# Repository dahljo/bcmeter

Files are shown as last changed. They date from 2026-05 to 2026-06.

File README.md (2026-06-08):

## Legacy maintenance notice

This repository remains online so existing legacy Raspberry Pi bcMeter devices can keep updating from it. Its project status is **legacy maintenance**: it receives compatibility fixes for already deployed devices, but it is no longer the current Raspberry Pi bcMeter codebase.

For new setups and long-term maintenance, use the redesigned Raspberry Pi version: https://github.com/dahljo/bcmeter-pi.

The redesigned version was built from scratch for better maintainability, reliability, and setup/update workflows. Complete ready-to-flash Raspberry Pi images are available from https://bcmeter.org. Contact jd@bcmeter.org for questions.

## Thank you for your interest! This repository contains everything you need to build your own bcMeter (DIY) — freely available for private, educational and research use under CC BY-NC 4.0. For commercial use and licensing, please contact jd@bcmeter.org.

## Recommended software setup:
download bcMeter.img from https://bcmeter.org and clone that to a microSD card - change WiFi credentials within bcMeters hotspot mode and you're ready.

## manual software setup:

see https://bcmeter.org/wiki/index.php?title=Installation#Alternative:_Manual_Set_Up_the_microSD_Card for instructions, the basic procedure is:

1. write raspberry LITE(!) image to micro sd card with the help of the imager (https://www.raspberrypi.com/news/raspberry-pi-imager-imaging-utility/) - use the imager to configure SSH and WiFi BEFORE starting the write process!
2. bootup raspberry pi and log into it via ssh, download and run install.sh script:
wget -N https://raw.githubusercontent.com/dahljo/bcmeter/main/install.sh && sudo bash install.sh
3. run bcMeter script

### Script / Interface

install.sh is a just a batch to configure the raspberry for the use as bcMeter
bcMeter.py is the python script which saves the data as csv
/interface contains a d3.js interface for reading out the csv file

### Gerber for PCB Manufactoring

in /gerbers you'll find the gerbers for PCB manufactoring.

### STL files for 3D Printing

in /stl you find the files for 3d printing.

bcMeter Case

bcMeter PCB

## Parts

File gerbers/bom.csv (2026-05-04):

Designator | Footprint | Quantity | Value
C1 | 805 | 1 | 100nF
C10, C11, C12 | 805 | 3 | 1uF
C13 | 805 | 1 | 15nF
C15, C22 | 805 | 2 | 220pF
C16, C4 | 805 | 2 | 100nF
C17 | 805 | 1 | 10uF
C18 | 805 | 1 | 0.1uF
C20 | 1210 | 1 | 47uF
C21 | CP_Elec_6.3x5.8 | 1 | 470uF
C6, C9 | 805 | 2 | 5.6pF
D10, D11, D4, D6, D7 | D_SOD-123 | 5 | 1N5817
D12 | D_SMB | 1 | B230
D3 | 805 | 1 | Status LED
D5 | D_SMA | 1 | SS24
J1 | JST_SH_SM03B-SRSS-TB_1x03-1MP_P1.00mm_Horizontal | 1 | Omron D6F
J11 | JST_PH_B4B-PH-K_1x04_P2.00mm_Vertical | 1 | DISP
J12 | PinHeader_2x03_P2.54mm_Vertical | 1 | Conn_02x03_Counter_Clockwise
J13 | PinHeader_1x02_P2.54mm_Vertical | 1 | 5V Ext
J15 | BarrelJack_GCT_DCJ200-10-A_Horizontal | 1 | Jack-DC
J16, J18, J19, J20 | JST_EH_B4B-EH-A_1x04_P2.50mm_Vertical | 4 | Conn_01x04
J17 | JST_PH_B2B-PH-K_1x02_P2.00mm_Vertical | 1 | 12V Header for non pwm pump
J2 | JST_PH_B4B-PH-K_1x04_P2.00mm_Vertical | 1 | i2c opt
J3 | PinHeader_1x02_P2.54mm_Vertical | 1 | 3.3V Header
J5 | JST_XH_B2B-XH-A_1x02_P2.50mm_Vertical | 1 | Pump 5V Header NONPWM
J6 | PinSocket_2x20_P2.54mm_Vertical | 1 | Raspberry_Pi_2_3
J7 | JST_EH_B2B-EH-A_1x02_P2.50mm_Vertical | 1 | heater/fan
J8 | JST_XH_B3B-XH-A_1x03_P2.50mm_Vertical | 1 | Conn_01x03
L2 | L_Bourns_SRP7028A_7.3x6.6mm | 1 | 15uH
Q3, Q7, Q8 | SOT-23 | 3 | MMBT3904
Q4, Q5, Q6 | SOT-23 | 3 | AO3400A
R1, R2, R7 | 805 | 3 | 3k3
R11, R6 | 805 | 2 | 5K
R12, R13 | 805 | 2 | 100R
R14 | 805 | 1 | 10k2R
R15 | 805 | 1 | 1k7
R19, R4 | 805 | 2 | 150
R20, R21 | 805 | 2 | 75
R22, R25, R5 | 805 | 3 | 10k
R23, R24 | 805 | 2 | 68
R26, R27 | 805 | 2 | 100k
R3 | 805 | 1 | 5
R8 | 805 | 1 | 30.9K
SW1 | PinHeader_2x01_P2.54mm_Vertical | 1 | Button
U1 | SOIC-8_3.9x4.9mm_P1.27mm | 1 | MCP6022
U3 | Sensirion_DFN-4_1.5x1.5mm_P0.8mm_SHT4x_NoCentralPad | 1 | SHT4x
U4 | SSOP-20_3.9x8.7mm_P0.635mm | 1 | ADS8344N
U5 | SOIC-8-1EP_3.9x4.9mm_P1.27mm_EP2.62x3.51mm | 1 | TPS54233
U6 | SOIC-8_3.9x4.9mm_P1.27mm | 1 | MCP1501-40xSN

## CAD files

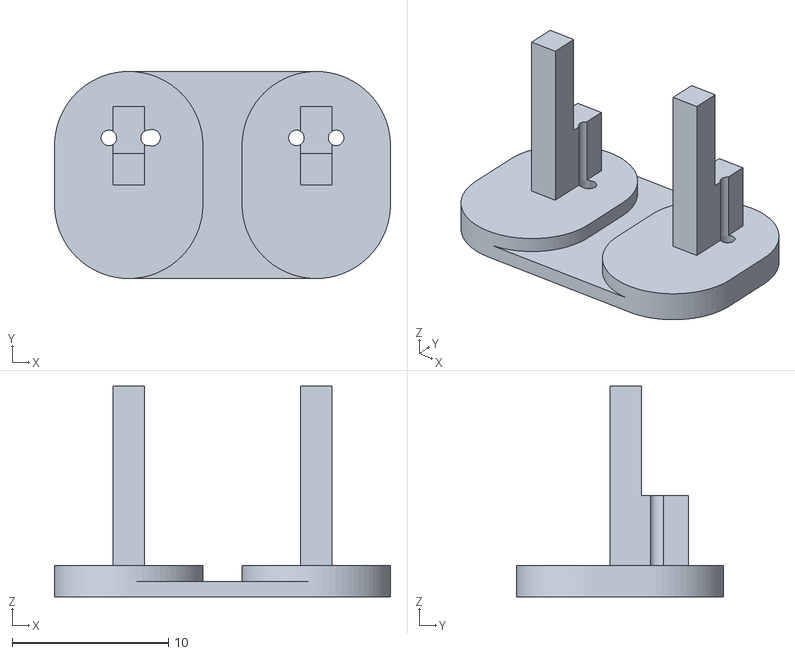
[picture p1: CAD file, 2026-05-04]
stl/bcMeter_sensorbracket.stl
21.5 x 13.2 x 13.5

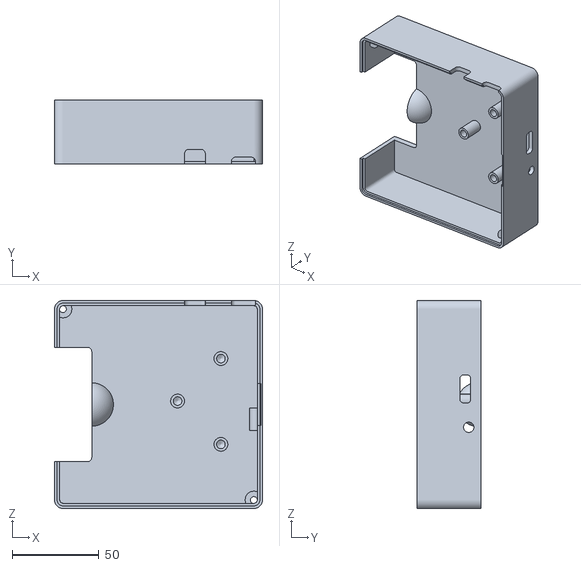
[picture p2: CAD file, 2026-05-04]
stl/bcMeter_iot_topcase.stl
120.0 x 37.0 x 120.0

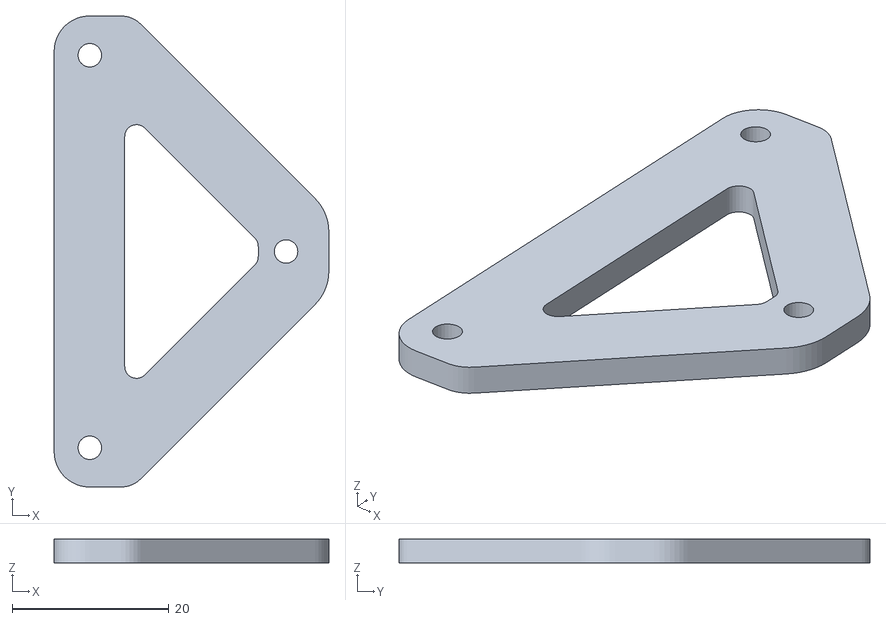
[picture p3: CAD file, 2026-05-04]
stl/bcmeter-sps30-bracket.stl
35.0 x 60.0 x 3.00

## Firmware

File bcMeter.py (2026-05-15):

import glob
import os
import re
import signal
import socket
import shutil
import subprocess
import sys
import typing
from collections import deque
from datetime import datetime
from pathlib import Path
from threading import Thread, Event, Lock
from time import sleep, time

import numpy
import pigpio
import RPi.GPIO as GPIO
import smbus
import spidev

from bcMeter_shared import (
	config_json_handler,
	check_connection,
	manage_bcmeter_status,
	show_display,
	config,
	i2c,
	setup_logging,
	run_command,
	send_email,
	update_config,
	filter_values_ona,
	apply_dynamic_airflow,
	can_send_mail,
	get_session_flag,
	set_session_flag
)

sps30_available = False
sps30_sensor = None

bcMeter_version = "1.1.5 2026-05-15"
base_dir = '/home/bcmeter' if os.path.isdir('/home/bcmeter') else '/home/bcMeter' if os.path.isdir('/home/bcMeter') else '/home/pi'

logger = setup_logging('bcMeter')
debug = True if (len(sys.argv) > 1) and (sys.argv[1] == "debug") else False
if debug:
	logger.debug("--- DEBUG MODE ENABLED ---")
logger.debug(config)
logger.debug(f"bcMeter Version {bcMeter_version}")
bus = smbus.SMBus(1)
i2c_lock = Lock()

import bcMeter_shared
bcMeter_shared.i2c_lock = i2c_lock

try:
	from sps30_i2c import SPS30
	_sps = SPS30(bus=1, i2c_lock=i2c_lock)
	_sps.start()
	sleep(1)
	for _ in range(5):
		if _sps.data_ready():
			sps30_available = True
			sps30_sensor = _sps
			break
		sleep(0.5)
	if not sps30_available:
		_sps.stop()
		_sps.close()
except Exception as e:
	if debug:
		print(f"SPS30 init failed: {e}")
	sps30_available = False

if sps30_available:
	logger.info("SPS30 PM sensor detected and initialized")

NUM_CHANNELS = config.get('num_channels', 1)
LED_880NM_PIN = 26
LED_520NM_PIN = 25
LED_370NM_PIN = 24
BUSY_PIN = 17

CHANNELS_CONFIG = {
	'880nm': {'pin': LED_880NM_PIN, 'sigma': 7.77e-8, 'sens': 0, 'ref': 0, 'atn': 0, 'bc': 0, 'bc_unfiltered': 0},
	'520nm': {'pin': LED_520NM_PIN, 'sigma': 13.14e-8, 'sens': 0, 'ref': 0, 'atn': 0, 'bc': 0, 'bc_unfiltered': 0},
	'370nm': {'pin': LED_370NM_PIN, 'sigma': 18.47e-8, 'sens': 0, 'ref': 0, 'atn': 0, 'bc': 0, 'bc_unfiltered': 0},
}
WAVELENGTH_ORDER = ['880nm', '520nm', '370nm']

disable_pump_control = config.get('disable_pump_control', False)
get_location = config.get('get_location', False)
heating = config.get('heating', False)
pump_pwm_freq = int(config.get('pwm_freq', 20))
af_sensor_type = int(config.get('af_sensor_type', 1))
use_rgb_led = config.get('use_rgb_led', 0)
use_display = config.get('use_display', False)
airflow_sensor = config.get('airflow_sensor', False)
pump_dutycycle = int(config.get('pump_dutycycle', 20))
reverse_dutycycle = config.get('reverse_dutycycle', False)
sample_spot_diameter = float(str(config.get('sample_spot_diameter', 0.4)).replace(',', '.'))
is_ebcMeter = config.get('is_ebcMeter', False)
mail_logs_to = config.get('mail_logs_to', "")
send_log_by_mail = config.get('send_log_by_mail', False)
filter_status_mail = config.get('filter_status_mail', False)
disable_led = config.get('disable_led', False)
airflow_type = int(config.get('af_sensor_type', 1))
TWELVEVOLT_ENABLE = config.get('TWELVEVOLT_ENABLE', False)
twelvevolt_duty = config.get('twelvevolt_duty', 20)
automatic_airflow_control = config.get('automatic_airflow_control', False)
spi_vref=config.get('spi_vref', 4.096)

iot_enable=config.get('iot_enable', False)

bc_data_history = {
	'unfiltered': {wl: [] for wl in WAVELENGTH_ORDER},
	'filtered': {wl: [] for wl in WAVELENGTH_ORDER},
	'all_log_data': []
}
current_measured_airflow_lpm = 0.0
desired_airflow_in_lpm = float(str(config.get('airflow_per_minute', 0.1)).replace(',', '.'))

_bc_filter_state = {}

def filter_bc_values():
	global bc_data_history, is_ebcMeter, WAVELENGTH_ORDER, _bc_filter_state
	kernel = 3 if is_ebcMeter else 5
	state = _bc_filter_state
	if state.get('kernel') != kernel or not state.get('windows'):
		state['kernel'] = kernel
		state['windows'] = {wl: deque(maxlen=kernel) for wl in WAVELENGTH_ORDER}
		state['processed'] = {wl: 0 for wl in WAVELENGTH_ORDER}
		for wl in WAVELENGTH_ORDER:
			bc_data_history['filtered'][wl] = []
	for wl in WAVELENGTH_ORDER:
		unfiltered = bc_data_history['unfiltered'][wl]
		processed = state['processed'].get(wl, 0)
		if processed > len(unfiltered):
			processed = 0
			state['windows'][wl].clear()
			bc_data_history['filtered'][wl] = []
		window = state['windows'][wl]
		for v in unfiltered[processed:]:
			window.append(v)
			med = numpy.median(list(window))
			bc_data_history['filtered'][wl].append(float(med) if is_ebcMeter else int(med))
		state['processed'][wl] = len(unfiltered)


class ADS8344:
	START_BIT = 0x80
	SINGLE_END = 0x04
	CLOCK_INTERNAL = 0x02
	CHANNELS = {
		0: 0x00, 1: 0x04, 2: 0x01, 3: 0x05,
		4: 0x02, 5: 0x06, 6: 0x03, 7: 0x07
	}

	def __init__(self, bus=0, device=0, vref=spi_vref, busy_pin=None):
		self.spi = spidev.SpiDev()
		self.busy_pin = busy_pin
		try:
			self.spi.open(bus, device)
			self.spi.max_speed_hz = 1000000
			self.spi.mode = 0
			self.vref = vref
			if self.busy_pin is not None:
				GPIO.setup(self.busy_pin, GPIO.IN, pull_up_down=GPIO.PUD_UP)
			self.initialized = True
		except Exception as e:
			logger.error(f"Failed to initialize SPI: {e}")
			self.initialized = False

	def close(self):
		if hasattr(self, 'spi') and self.spi is not None:
			self.spi.close()

	def read_channel(self, channel):
		if not self.initialized:
			return -1, None
		try:
			channel_bits = (self.CHANNELS[channel] & 0x7) << 4
			cmd = self.START_BIT | self.SINGLE_END | channel_bits | self.CLOCK_INTERNAL
			self.spi.writebytes([cmd])

			if self.busy_pin is not None:
				while GPIO.input(self.busy_pin) == GPIO.LOW:
					pass

			result = self.spi.readbytes(3)
			value = (result[0] << 9) | (result[1] << 1) | (result[2] >> 7)
			voltage = (value / 65536.0) * self.vref
			return voltage, result
		except Exception as e:
			logger.error(f"SPI read error: {e}")
			return -1, None

	def read_all_channels(self):
		if not self.initialized:
			return {}
		results = {}
		try:
			for ch in self.CHANNELS.keys():
				voltage, _ = self.read_channel(ch)
				if voltage != -1:
					results[f"CH{ch}"] = voltage
			return results
		except Exception as e:
			logger.error(f"SPI batch read error: {e}")
			return {}




if airflow_type == 9:
	from bcMeter_shared import read_airflow_ml
cooling = False
temperature_to_keep = 35 if cooling is False else 0
run_once = "false"
airflow_debug = True if (len(sys.argv) > 1) and (sys.argv[1] == "airflow") else False
sht40_i2c = None
online = False
output_to_terminal = False
use_spi = False
spi_adc = None

show_display(f"Initializing bcMeter", False, 0)
show_display(f"bcMeter {bcMeter_version}", False, 1)

GPIO.setmode(GPIO.BCM)
devicename = socket.gethostname()
sample_spot_areasize=numpy.pi*(float(sample_spot_diameter)/2)**2
os.chdir(base_dir)
calibration = True if (len(sys.argv) > 1) and (sys.argv[1] == "cal") else False
GPIO.setmode(GPIO.BCM)
MONOLED_PIN=1
PUMP_PIN = 12
TWELVEVOLT_PIN = 27
GPIO.setup(MONOLED_PIN, GPIO.OUT)

if TWELVEVOLT_ENABLE:
	GPIO.setup(TWELVEVOLT_PIN, GPIO.OUT)

MCP342X_DEFAULT_ADDRESS = 0x68
MCP342X_GENERAL_CALL_RESET = 0x06
VOLTAGE_REFERENCE = 2.048

MCP342X_CONFIG_READY = 0x80
MCP342X_CONFIG_MODE_ONESHOT = 0x00
MCP342X_CONFIG_MODE_CONTINUOUS = 0x10
MCP342X_CONFIG_CH1 = 0x00
MCP342X_CONFIG_CH2 = 0x20
MCP342X_CONFIG_CH3 = 0x40
MCP342X_CONFIG_CH4 = 0x60
MCP342X_CONFIG_SPS_240_12BIT = 0x00
MCP342X_CONFIG_SPS_60_14BIT = 0x04
MCP342X_CONFIG_SPS_15_16BIT = 0x08
MCP342X_CONFIG_GAIN_1X = 0x00
MCP342X_CONFIG_GAIN_2X = 0x01
MCP342X_CONFIG_GAIN_4X = 0x02
MCP342X_CONFIG_GAIN_8X = 0x03

adc_rate = MCP342X_CONFIG_SPS_60_14BIT
adc_gain = MCP342X_CONFIG_GAIN_1X

airflow_only = True if (len(sys.argv) > 1) and (sys.argv[1] == "airflow") else False
airflow_channel = MCP342X_CONFIG_CH1 if airflow_only is True and sys.argv[1] == "1" else MCP342X_CONFIG_CH3
sampling_thread = housekeeping_thread = airflow_control_thread = None

stop_event = Event()
change_blinking_pattern = Event()

PUMP_PWM_RANGE = 100 if reverse_dutycycle else 255
PUMP_PWM_FREQ = int(config.get('pwm_freq', 20))
LED_PWM_RANGE = 255
LED_PWM_FREQ = 1000




def gradual_shutdown_12v(steps=20, step_delay=0.25):
	global pi, TWELVEVOLT_PIN
	try:
		if not (pi and pi.connected):
			return

		current_duty = pi.get_PWM_dutycycle(TWELVEVOLT_PIN)
		if current_duty == 0:
			return

		step_size = current_duty / steps
		for i in range(steps):
			if not pi.connected:
				logger.warning("pigpio disconnected during 12V shutdown.")
				break

			reduced_duty = max(0, int(current_duty - (step_size * (i + 1))))
			pi.set_PWM_dutycycle(TWELVEVOLT_PIN, reduced_duty)
			sleep(step_delay)

		if pi.connected:
			pi.set_PWM_dutycycle(TWELVEVOLT_PIN, 0)

		logger.debug("12V power ramp-down complete or was interrupted.")
	except Exception as e:
		logger.error(f"Error during 12V gradual shutdown: {e}")
		try:
			if pi and pi.connected:
				pi.set_PWM_dutycycle(TWELVEVOLT_PIN, 0)
		except:
			pass

def shutdown(reason, shutdown_code=None):
	global reverse_dutycycle, housekeeping_thread, airflow_control_thread, sampling_thread, TWELVEVOLT_ENABLE
	global spi_adc, use_spi, sps30_sensor, sps30_available
	stop_event.set()
	change_blinking_pattern.set()
	print(f"Quitting: {reason}")
	logger.debug(f"Shutdown initiated: {reason}")

	if sps30_available and sps30_sensor:
		try:
			sps30_sensor.stop()
			sps30_sensor.close()
		except Exception:
			pass

	try:
		if _archive_logger is not None:
			_archive_logger.close()
		if _current_logger is not None:
			_current_logger.close()
	except Exception:
		pass

	show_display("Goodbye", 0, True)
	if reason == "SIGINT" or reason == "SIGTERM":
		show_display("Turn off bcMeter", 1, True)
	else:
		show_display(f"{reason}", 1, True)
	show_display("", 2, True)

	if use_spi and spi_adc is not None:
		try:
			spi_adc.close()
			logger.debug("SPI ADC connection closed")
		except Exception as e:
			logger.error(f"Error closing SPI ADC: {e}")

	if reason != "Already running":
		try:
			if 'pi' in globals() and pi.connected:
				if TWELVEVOLT_ENABLE:
					 gradual_shutdown_12v()
					 sleep(1)
				if reverse_dutycycle is False:
					try:
						pi.set_PWM_dutycycle(PUMP_PIN, 0)
					except:
						pass
				else:
					try:
						pi.set_PWM_dutycycle(PUMP_PIN, PUMP_PWM_RANGE)
					except:
						pass
				pi.stop()
				logger.debug("pigpio connection stopped")
				try:
					subprocess.run(["sudo", "killall", "pigpiod"], check=False, timeout=2)
					logger.debug("pigpiod process terminated")
				except subprocess.TimeoutExpired:
					logger.warning("Timeout while trying to kill pigpiod")
		except Exception as e:
			logger.error(f"Error stopping pigpio: {e}")

	from threading import current_thread
	current_thread_id = current_thread().ident
	threads_to_join = []
	if sampling_thread and sampling_thread.is_alive() and sampling_thread.ident != current_thread_id:
		threads_to_join.append(sampling_thread)
	if housekeeping_thread and housekeeping_thread.is_alive() and housekeeping_thread.ident != current_thread_id:
		threads_to_join.append(housekeeping_thread)
	if airflow_control_thread and airflow_control_thread.is_alive() and airflow_control_thread.ident != current_thread_id:
		threads_to_join.append(airflow_control_thread)
	for thread in threads_to_join:
		thread.join(timeout=1)
		if thread.is_alive():
			logger.warning(f"Thread {thread.name} didn't terminate within timeout")

	if shutdown_code is None:
		shutdown_code = 5
	manage_bcmeter_status(action='set', bcMeter_status=shutdown_code)

	try:
		GPIO.cleanup()
		logger.debug("GPIO cleanup completed")
	except Exception as e:
		logger.error(f"Error during GPIO cleanup: {e}")
	sys.exit(0)
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

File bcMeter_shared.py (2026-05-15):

import json, socket, os, busio, logging, subprocess, re, time, csv
from board import I2C, SCL, SDA
from datetime import datetime
import RPi.GPIO as GPIO
import smtplib
from email.mime.text import MIMEText
from email.mime.multipart import MIMEMultipart
from email.mime.application import MIMEApplication
import platform
import shutil
import numpy as np

bcMeter_shared_version = "1.4.1 2026-05-15"

i2c = busio.I2C(SCL, SDA)
base_dir = '/home/bcmeter' if os.path.isdir('/home/bcmeter') else '/home/bcMeter' if os.path.isdir('/home/bcMeter') else '/home/pi'

hostname = socket.gethostname()

CONNECTION_PRIMARY = {"host": "www.google.com", "port": 80}
CONNECTION_TIMEOUT = 3
CONNECTION_TRIES = 3
CONNECTION_RETRY_SLEEP = 2

def check_connection(wifi_only=True):
	result = subprocess.run(['ip', 'route'], capture_output=True, text=True)
	if "default" not in result.stdout:
		return False
	if wifi_only:
		if "wlan0" not in result.stdout and "wlan1" not in result.stdout:
			return False
	for attempt in range(CONNECTION_TRIES):
		try:
			s = socket.create_connection((CONNECTION_PRIMARY["host"], CONNECTION_PRIMARY["port"]), timeout=CONNECTION_TIMEOUT)
			s.close()
			return True
		except Exception:
			if attempt < CONNECTION_TRIES - 1:
				time.sleep(CONNECTION_RETRY_SLEEP)
	return False

def setup_logging(log_entity):
	log_folder = base_dir + '/maintenance_logs/'
	os.makedirs(log_folder, exist_ok=True)
	logger = logging.getLogger(f'{log_entity}_log')
	logger.setLevel(logging.DEBUG)
	logger.handlers.clear()
	log_file_generic = os.path.join(log_folder, f'{log_entity}.log')
	if os.path.exists(log_file_generic):
		os.remove(log_file_generic)
	handler_generic = logging.FileHandler(log_file_generic)
	handler_generic.setLevel(logging.DEBUG)
	formatter_generic = logging.Formatter('%(asctime)s - %(levelname)s: %(message)s')
	handler_generic.setFormatter(formatter_generic)
	current_datetime = datetime.now().strftime("%Y-%m-%d_%H-%M-%S")
	log_file_timestamped = os.path.join(log_folder, f'{log_entity}_{current_datetime}.log')
	handler_timestamped = logging.FileHandler(log_file_timestamped)
	handler_timestamped.setLevel(logging.DEBUG)
	formatter_timestamped = logging.Formatter('%(asctime)s - %(levelname)s: %(message)s')
	handler_timestamped.setFormatter(formatter_timestamped)
	logger.addHandler(handler_generic)
	logger.addHandler(handler_timestamped)
	prefix_to_match = f"{log_entity}_"
	log_files = []
	for f in os.listdir(log_folder):
		if not f.endswith('.log'):
			continue
		if not f.startswith(prefix_to_match):
			continue
		remainder = f[len(prefix_to_match):]
		if len(remainder) > 0 and remainder[0].isdigit():
			log_files.append(f)
	log_files.sort()
	if len(log_files) > 10:
		for file_to_remove in log_files[:len(log_files) - 10]:
			try:
				os.remove(os.path.join(log_folder, file_to_remove))
			except OSError:
				pass
	logger.debug(f"Logging setup complete for {log_entity}")
	return logger

logger = setup_logging('bcMeter_shared')

def run_command(command):
	try:
		result = subprocess.run(command.split(), capture_output=True, text=True)
		if result.returncode != 0:
			logger.error(f"Error in {command}: {result.stderr}")
			return None
		return result.stdout.strip()
	except Exception as e:
		logger.error(f"Exception running command '{command}': {e}")
		return None
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

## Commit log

2021-07-07 Add files via upload
    general purpose case for 12v psu and large pumps (can be used with usb only and smaller pumps as well)
    [290621_bottomCase.stl, 290621_intake.stl, 290621_sensorBracket-print2.stl, 290621_topCase-noDisplay.stl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]
2021-10-08 Create current.csv
    sample to test the interface
    [current.csv]
2022-05-10 Updated Rev 3 Gerber-Files
    Rev 3 of the PCB: Connector for Heater, more i2c header, use of ubiquitary DSB18B20 temperature sensor, display connector, 3V3 and 5V general purpose header
2023-02-21 Hotspot Mode and Updates/Fixes
    Updates and Fixes
    * Hotspot mode - no need to save wifi credentials on SD Card anymore!
    * MUCH easyer log access through the interface
    * Control the pump (new PCB required) within the interface
    * Upload data optionally to CompAIR
    Updates
2023-03-11 0.9.25
    Changed PWM Frequency of pump for stability, bug in interface,
2024-02-07 Accuracy improvements
    Big update, approaching 1.0!
    Crucial compatibility / accuracy update
    This is a major overhaul of everything.
    * rework of the interface
    * reworked sample requesting function
    * reworked FROST implementation
    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
    [bcMeter-bottomcase.stl, bcMeter-filter-top.stl, bcMeter-led-top-print2times.stl, bcMeter-sensor-bottom-print2times.stl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]
2024-04-17 Usability / Interface changes
    * Added optional calibration after filter swap
    * outsourced functions to a shared file (thanks @d-roet for the final spark to do this by delivering an updated online-check)
    * Completely rewrote the "Options" interaction between interface and python
    * Completely rewrote the status function by now using flask
    * After 3 years I may finally have achieved a stable wifi / hotspot mechanism - found a few issues and fixed them. Lets see :-)
2024-06-21 bug fix and small additions
    Fixed a crucial bug where the config could have been overwritten with empty file (that's how we say to "accidentally deleted")
    I am testing the idea of using a fan instead of a heater. so, why not both. Fans are 10x more energy efficient and seem to solve the problem with heat spikes more reliable than the heater.
    further reorganization of the shared functions.
    updated install routine and log.
2024-06-21 Updated 3D files
    updated the STL Files for the small cas
    discarded the big case
    [bcMeter-bottomcase.stl, bcMeter-filter-top.stl, bcMeter-led-top-print2times.stl, bcMeter-sensor-bottom-print2times.stl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]
2024-08-13 Case Update
    Usability improvements of the bcMeter Case
    [bcMeter_bottomcase_handscrew v15.stl, bcMeter_bottomcase_handscrew v8.stl, bcMeter_ledholder_handscrew v3.stl, bcMeter_ledholder_handscrew v8.stl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]
2024-08-13 Update bcMeter_sensorbracket v3.stl
    [bcMeter_sensorbracket v3.stl]
2024-08-20 Accuracy improvements
    Calibrated airflow
2024-10-29 Interface and connectivity improvements
    Reworked the Hotspot / Wifi functionality and fixed lots of usability issues within the interface.
    A new feature is to display a warning for undervoltage. This happens a lot and is a common cause for the raspberry pi to run unstable, crash oftn and reboot.
2024-11-25 Case Design update
    Usability and assembly improvements.
    Use M4 Threads for the LED top part and 30mm M4 Screws. Other holes are made for M3 threads (5mm)
    [bcMeter_bottomcase_handscrew v15.stl, bcMeter_bottomcase_handscrew v29.stl, bcMeter_ledholder_handscrew v15.stl, bcMeter_ledholder_handscrew v8.stl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]
2024-12-11 Bugfixes
    The status of the device was not sometimes not properly reflected within the status.
2025-02-18 Stability & UI Improvements
    More granular feedback on bcMeter Status for troubleshooting.
    Improved status mail sending functionality.
    Important: To be able to receive mails, there has to be a password set. As this repo is open source, anyone could use the mailer so this is not set by default. Just contact me.
    The device renames its wifi after the device name. Now more than one device can run next to each other.
    WiFi in general is more robust now.
2025-03-14 WiFi / Code / Stability
    * WiFi Connection issues when signal is lost were tracked down.
    * Fixed a bug where the pump did not shutdown properly
    * Added again more granular logging to be able to bugfix better
    * First step in modernizing the plotting was done, cleaned up the code and separated it from the plotting code. Migration to a better suiting framework is the next step.
2025-04-04 Accuracy and Stability Updates
    * More robust bias compensation
    * Experimental load dependent Airflow control (currently disabled by default
    * solved lots of interface bugs
    * Updated installer / Updater
    *Updated WiFi Error Handling
2025-04-11 Case update
    Using M4 30mm screws for case now and M4 threads which improves the sturdiness a whole lot.
    Other screw threads are M3 as before.
    [bcMeter_bottomcase_handscrew v29.stl, bcMeter_bottomcase_handscrew v55.stl, bcMeter_ledholder_handscrew v15.stl, bcMeter_ledholder_handscrew v25.stl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]
2025-07-25 Interface / WiFi / Sampling method update
    * Updated the Interface for better usability / stability and responsiveness
    * Improved reconnection robustness for lost / weak WiFi Signal (neverending story)
    * Added support for SPI ADC ADS8344E; this will enable future bcMeter products to sample multiple wavelengths
    * Future bcMeter hardware revisions can be optionally use 12V; added support to control 12V Pump for higher air volumes
2025-11-02 Installer & Interface bug fixes
    * in debian trixie, pigpiod is not in repository so it has to be installed manually for now
    * there was a bug displaying and evaluating the filter status in interface
    * e-mail sending of logs was not called properly after the last update.
2025-11-08 Brought back the function to rename the device from interface
2025-11-26 Improved Calibration
    Calibration now finds the optimal duticycle itself
2025-11-26 Updated installer to work with newest Raspberry OS
    In debian trixie, pigpio is as of today not part of the repository so it has to be built from source.
2026-05-04 Raspi Pi Gerbers + Case files updated
    Optimized Case for Sealing and fixation.
    Updated Pi Gerbers + BOM
    [bcMeter_bottomcase_handscrew v55.stl, bcMeter_iot_topcase.stl, bcMeter_ledholder_handscrew v25.stl, bcMeter_sensorbracket.stl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]
